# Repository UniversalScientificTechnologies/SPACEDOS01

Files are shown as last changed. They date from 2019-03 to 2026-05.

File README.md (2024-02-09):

# SPACEDOS01B - Cosmic-ray spectrometer and dosimeter for unmanned spacecraft missions

SPACEDOS01B is a semiconductor-based dosimeter launched at Sokrat-R (NORAD ID 44404) satellite, currently orbiting the Earth about 500km above the surface.
The device is intended for the measurement of cosmic radiation in mixed ionization fields on board satellites. In the case of manned missions look to [SPACEDOS02](https://github.com/UniversalScientificTechnologies/SPACEDOS02) or [SPACEDOS03](https://github.com/UniversalScientificTechnologies/SPACEDOS03).

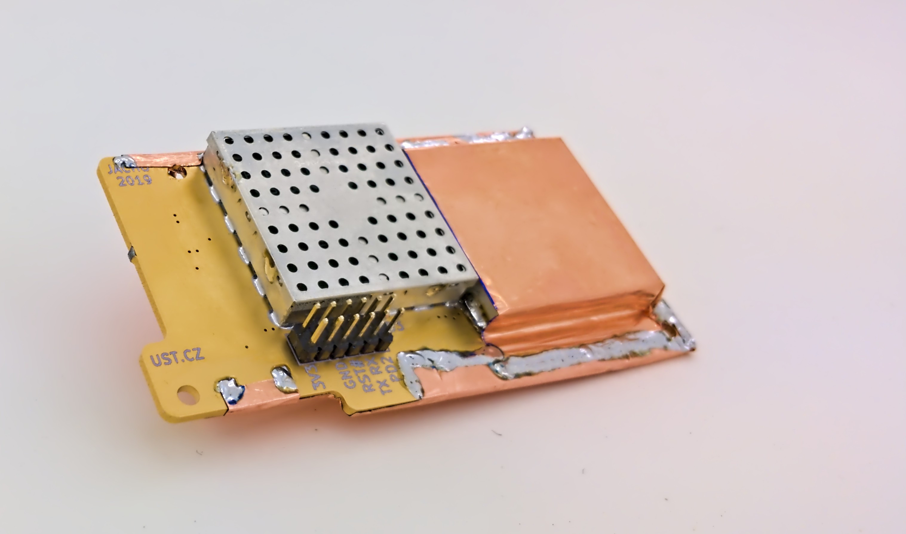
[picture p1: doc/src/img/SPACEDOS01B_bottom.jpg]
SPACEDOS01B device from bottom side PCB

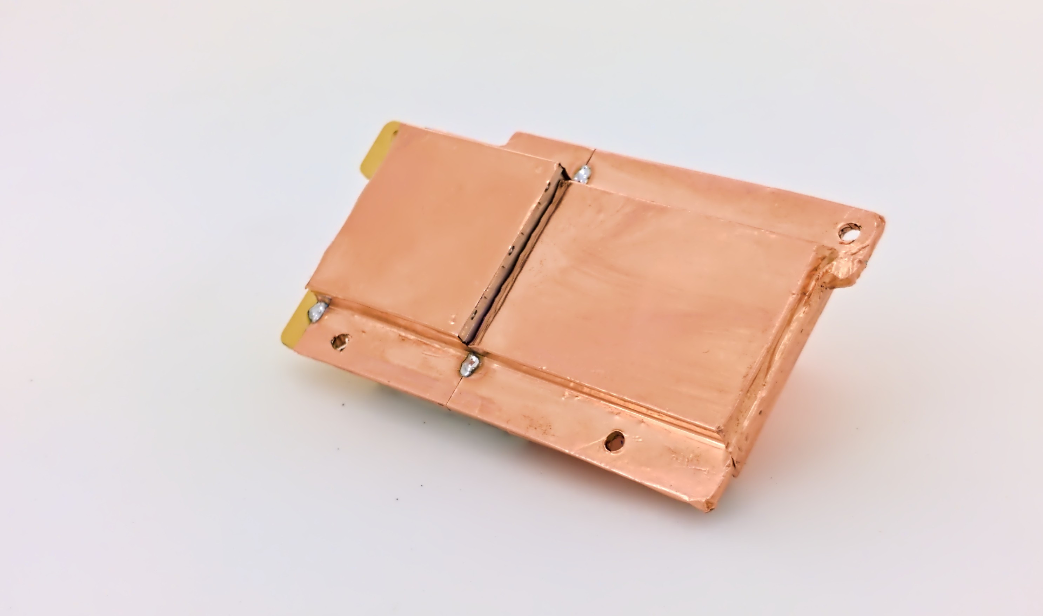
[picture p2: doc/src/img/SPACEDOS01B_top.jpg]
SPACEDOS01B device from top side PCB


The device can be purchased from Universal Scientific Technologies s.r.o. Contact us by email at sale@ust.cz for a commercial quotation.

### The main technical parameters are the following

* Silicon PIN diode detector with ~12.5 mm³ detection volume
* Measurement environment: vacuum < 3.2×10e−2 Pa
* Number of energy channels: 250
* Deposited energy range: from 200 keV to 12 MeV
* Energy measurement resolution: < 50 keV/channel
* Power supply: 3.3 V / 3 mA
* Integration time: 15 s
* Interface: RS232 TTL
* Dimensions(HxWxL): 15mm x 41mm x 94 mm
* Weight 33 g

[Technical documentation](https://docs.dos.ust.cz/spacedos/SPACEDOS01)

## References

  * [SPACEDOS dosimeter from the NPI became a part of the Cosmos Discovery exhibition](http://www.ujf.cas.cz/en/news/SPACEDOS-dosimeter-from-the-NPI-became-a-part-of-the-Cosmos-Discovery-exhibition/)
  * [SPACEDOS an open-source PIN diode dosimeter for applications in Space](https://indico.ujf.cas.cz/event/2/contributions/27/attachments/25/46/Po-1315-Kakona-774711333.pdf)

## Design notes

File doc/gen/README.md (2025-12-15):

# PCB

Board size: 93.5x48.16 mm (3.68x1.9 inches)

- This is the size of the rectangle that contains the board
- Thickness: 1.6 mm (63 mils)
- Material: FR4
- Finish: HAL
- Layers: 2
- Copper thickness: 35 µm

Solder mask: TOP / BOTTOM

- Color: Green

Silk screen: TOP / BOTTOM

- Color: White

# Important sizes

Clearance: 0.2 mm (8 mils)

Track width: 0.25 mm (10 mils)

- By design rules: 0.2 mm (8 mils)

Drill: 0.5 mm (20 mils)

- Vias: 0.5 mm (20 mils) [Design: 0.4 mm (16 mils)]
- Pads: 0.85 mm (33 mils)
- The above values are real drill sizes, they add 0.1 mm (4 mils) to plated holes (PTH)

Via: 0.8/0.4 mm (31/16 mils)

- By design rules: 0.8/0.3 mm (31/12 mils)
- Micro via: yes [0.2/0.1 mm (8/4 mils)]
- Buried/blind via: yes
- Total: 188 (thru: 188 buried/blind: 0 micro: 0)

Outer Annular Ring: 0.15 mm (6 mils)

- By design rules: 0.26 mm (10 mils)

Eurocircuits class: 4B
- Using min drill 0.5 mm for an OAR of 0.15 mm

# General stats

Components count: (SMD/THT)

- Top: 73/9 (SMD + THT)
- Bottom: 2/8 (SMD + THT)

Defined tracks:

- 0.3 mm (12 mils)
- 0.4 mm (16 mils)
- 0.5 mm (20 mils)
- 0.6 mm (24 mils)
- 0.7 mm (28 mils)
- 0.8 mm (31 mils)

Used tracks:

- 0.25 mm (10 mils) (67) defined: no
- 0.3 mm (12 mils) (84) defined: yes
- 0.4 mm (16 mils) (246) defined: yes
- 0.5 mm (20 mils) (2) defined: yes
- 0.6 mm (24 mils) (34) defined: yes
- 0.8 mm (31 mils) (54) defined: yes

Defined vias:

Used vias:

- 0.8/0.4 mm (31/16 mils) (Count: 188, Aspect: 2.0 A) defined: no

Holes (excluding vias):

- 0.76 mm (30 mils) (2)
- 0.89 mm (35 mils) (12)
- 3.0 mm (118 mils) (4)

Oval holes:

Drill tools (including vias and computing adjusts and rounding):

- 0.5 mm (20 mils) (188)
- 0.85 mm (33 mils) (2)
- 1.0 mm (39 mils) (12)
- 3.1 mm (122 mils) (4)

Solder paste stats:

Using a paste with 87.75 % alloy, that has an specific gravity for the alloy of 7.4 g/cm³
and 1.0 g/cm³ for the flux. This paste has an specific gravity of  4.15 g/cm³.

The stencil thickness is  0.12 mm.

| Side   | Pads with paste | Area [mm²] | Paste [g] |
|--------|-----------------|------------|-----------|
| Top    |             280 |     466.08 |      2.32 |
| Bottom |              56 |     166.40 |      0.83 |
| Total  |             336 |     632.48 |      3.15 |

Note: this is just an approximation to the theoretical value. Margins of the solder mask and waste aren't computed.

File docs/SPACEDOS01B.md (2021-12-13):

---
layout: default
title: SPACEDOS01B
nav_order: 0
parent: SPACEDOS01
permalink: SPACEDOS01B
---

# SPACEDOS
## Physical dimensions
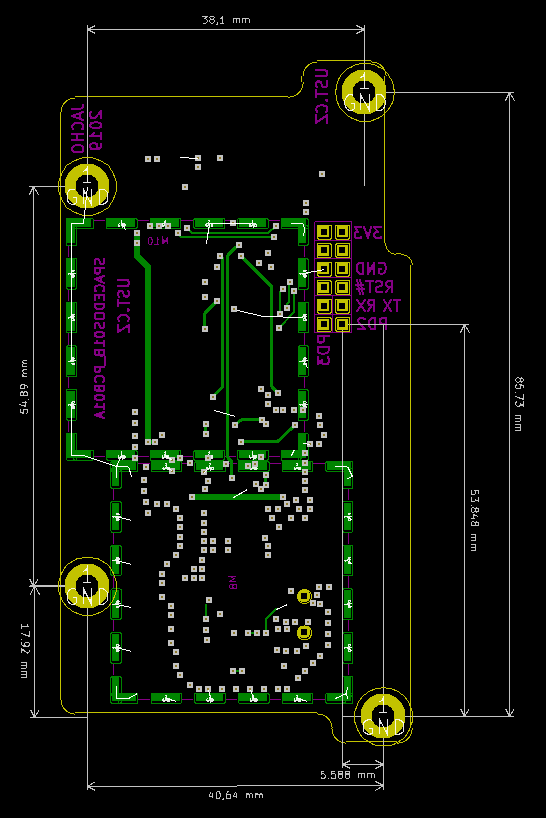
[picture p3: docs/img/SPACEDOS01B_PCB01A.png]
Physical dimensions


## Energetic range and Climatic endurance
 
 * Dissipated Energy range: from 100 keV to 9 MeV (divided into 8 logarithmic channels)
 * Energy Resolution: < 50 keV
 * Integration Time: 15 s
 * Temperature Stability: from -50 ℃ to +50 ℃ within error +50 keV
 * Used Sensor: HAMAMATSU S11773-02 (PIN diode 5 x 5 x 0.5 mm<sup>3</sup>)
 * Weight: 33 g

## Electrical interface
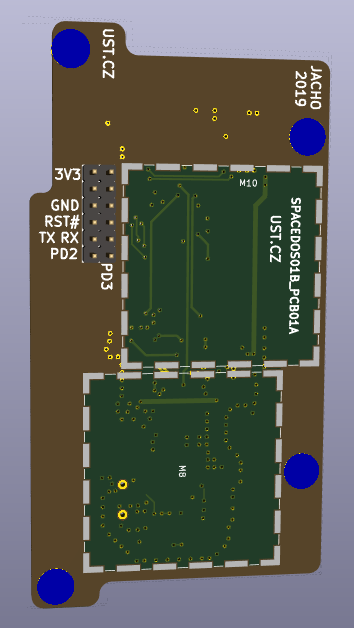
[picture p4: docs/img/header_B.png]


Conector is depicted from PIN's side.

Signal | Description
--- | ---
PD2 |  Universal Input pin
PD3 |  Universal Output pin
RX0 |  RS232 Receive (3.3 V)
TX0 |  RS232 Transmit (3.3 V)
RST# | Reset (trough capacitor)
GND |  Ground
3V3 |  Power supply +3.3 V

Power consumption: 2.6 mA from 3.3 V

## Communication protocol
### Sample of output data
```
$POSD,2a1c18d43c3937e40a3beb6c2855589b2d1a19e9
$ICSD
$DPSD,98,7fbd,36,1,0,0,0,0,0,0,100
$HKSD,9,98,800b,fe,0,0,7fbd,36,1,0,0,0,0,0,0,0,0,0,0,0,0,0,0,0,0,0,0,0,0,0,0,0,0,0,0,0,0,0,0,0,0,0,0,0,0,0,0,0,0,0,0,0,0,0
$BESD,4,e7,2,1,0,0,0,0,0
$ADSD,d3,3,0,0,0,0
```

SPACEDOS sends `$DPSD`, `$HKSD` and `$BESD` messages each cca 15 seconds.
`$ADSD` message is sended ones per one day.

Communication speed is 2400 baud.

### Power On
_It transmits just after power on._

```
#POSD, <git hash>
```

Value | Length | Type |Note
--- | --- | --- | ---
`$POSD` | 5 B | [Char](https://github.com/ODZ-UJF-AV-CR/SPACEDOS01/wiki/Char) | Header
git hash | 20 B | [Hex](https://github.com/ODZ-UJF-AV-CR/SPACEDOS01/wiki/Hex) | Git hash tag from source file

This information just says hello after power on.

### Initiation complete
_It transmits ones after initialisation after power on._

```
#ICSD
```

Initiation of the SPACEDOS HW is done.
Initiation is completed up to one second after power on.

### DPSD - SpaceDos Data Payload message
_It transmits every 15 seconds._

```
$DPSD, <uptime>, <noise channel>, <0.1 MeV>, <0.14 MeV>, <0.21 MeV>, <0.33 MeV>, <0.66 MeV>, <1.68 MeV>, <4.72 MeV>, <'>=9 MeV'>, <DC offset>
```

Value | Length | Type |Note
--- | --- | --- | ---
$DPSD | 5 B | [Char](https://github.com/ODZ-UJF-AV-CR/SPACEDOS01/wiki/Char) | Header
uptime | 4 B | [Hex](https://github.com/ODZ-UJF-AV-CR/SPACEDOS01/wiki/Hex) | Time from power on
noise channel | 2 B | [Hex](https://github.com/ODZ-UJF-AV-CR/SPACEDOS01/wiki/Hex) | this channel containing noise
0.1 MeV | 2 B | [Hex](https://github.com/ODZ-UJF-AV-CR/SPACEDOS01/wiki/Hex) | number of particles with absorbed energy above 0.1 MeV
... | ... | ... |
'>=9' MeV | 2 B | [Hex](https://github.com/ODZ-UJF-AV-CR/SPACEDOS01/wiki/Hex) | Overrange particles
DC offset | 2 B | [Hex](https://github.com/ODZ-UJF-AV-CR/SPACEDOS01/wiki/Hex) | Offset of ADC

This messages should be stored for long period and transmited to the ground as a batch.

Minimal data payload (without timemark) is 18 B per 15 s => 103680 B per day

### HKSD - SpaceDos HouseKeeping message
_It transmits every 15 seconds._

```
$HKSD, <measurement No.> , <uptime>, <filter suppressions>, <position of the 1-st channel>, <1-st ch.>, <2-nd ch.>, <3-rd ch.>,...
``` 

There is a packet with housekeeping information. Transmission of this packet is done besides other experiments hosekeeping data. Total length of this packet should be shorten. 

Value | Range | type |Note
--- | --- | --- | ---
$HKSD | fix | [Char](https://github.com/ODZ-UJF-AV-CR/SPACEDOS01/wiki/Char) | Header
measurement No. | 0..65535 | [Hex](https://github.com/ODZ-UJF-AV-CR/SPACEDOS01/wiki/Hex) |
uptime | 0..4294967295 | [Hex](https://github.com/ODZ-UJF-AV-CR/SPACEDOS01/wiki/Hex) |
filter suppressions | 0..65535 | [Hex](https://github.com/ODZ-UJF-AV-CR/SPACEDOS01/wiki/Hex) | Number of ussage of digital filter for double peak suppression
position of the 1-st channel | 0..511 | [Hex](https://github.com/ODZ-UJF-AV-CR/SPACEDOS01/wiki/Hex) |
1-st ch. | 0..65535 | [Hex](https://github.com/ODZ-UJF-AV-CR/SPACEDOS01/wiki/Hex) | Number of events in 1-st ch.
2-nd ch. | 0..65535 |  [Hex](https://github.com/ODZ-UJF-AV-CR/SPACEDOS01/wiki/Hex) |Number of events in 2-nd ch.
... | ... |
50-th ch. | 0..65535 |  [Hex](https://github.com/ODZ-UJF-AV-CR/SPACEDOS01/wiki/Hex) |Number of events in 50-th ch.

### BESD - SpaceDos BEacon message
_It transmits every 15 seconds. Values are zeroed after sending ADSD message._

```
$BESD,<counter>, <0.1 MeV>, <0.14 MeV>, <0.21 MeV>, <0.33 MeV>, <0.66 MeV>, <1.68 MeV>, <4.72 MeV>, <'>=9 MeV'>
```

This message contains cumulative data for beacon transmission.

Value | Length | Type |Note
--- | --- | --- | ---
$BESD | 5 B | [Char](https://github.com/ODZ-UJF-AV-CR/SPACEDOS01/wiki/Char) | Header
counter | 2 B | [Hex](https://github.com/ODZ-UJF-AV-CR/SPACEDOS01/wiki/Hex) | Number of the beacon message
0.1 MeV | 2 B | [Hex](https://github.com/ODZ-UJF-AV-CR/SPACEDOS01/wiki/Hex) | number of particles with absorbed energy above 0.1 MeV
0.14 MeV | 2 B | [Hex](https://github.com/ODZ-UJF-AV-CR/SPACEDOS01/wiki/Hex) | number of particles with absorbed energy above 0.14 MeV
... | ... | ... |
'>=9' MeV | 2 B | [Hex](https://github.com/ODZ-UJF-AV-CR/SPACEDOS01/wiki/Hex) | Overrange particles

### ADSD - SpaceDos Almanac Data message
_It transmits after 5760 beacon messages. (cca every one day)_

```
$ADSD, <0.1 MeV 1 day old>, <0.14 MeV one day old>, <0.66 MeV one day old>, <0.1 MeV two days old>, <0.14 MeV two days old>, <0.66 MeV two days old>
```

This message contains two days old data for the beacon transmission purposes.

Value | Length | Type |Note
--- | --- | --- | ---
$ADSD | 5 B | [Char](https://github.com/ODZ-UJF-AV-CR/SPACEDOS01/wiki/Char) | Header
0.1 MeV one day old | 4 B | [Hex](https://github.com/ODZ-UJF-AV-CR/SPACEDOS01/wiki/Hex) | number of particles with absorbed energy above 0.1 MeV one day before
0.14 MeV one day old | 4 B | [Hex](https://github.com/ODZ-UJF-AV-CR/SPACEDOS01/wiki/Hex) | number of particles with absorbed energy above 0.14 MeV one day before
0.66 MeV one day old | 4 B | [Hex](https://github.com/ODZ-UJF-AV-CR/SPACEDOS01/wiki/Hex) | number of particles with absorbed energy above 0.66 MeV one day before
0.1 MeV two days old | 4 B | [Hex](https://github.com/ODZ-UJF-AV-CR/SPACEDOS01/wiki/Hex) | number of particles with absorbed energy above 0.1 MeV two days before
0.14 MeV two days old | 4 B | [Hex](https://github.com/ODZ-UJF-AV-CR/SPACEDOS01/wiki/Hex) | number of particles with absorbed energy above 0.14 MeV two days before
0.66 MeV two days old | 4 B | [Hex](https://github.com/ODZ-UJF-AV-CR/SPACEDOS01/wiki/Hex) | number of particles with absorbed energy above 0.66 MeV two days before

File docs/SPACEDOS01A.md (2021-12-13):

---
layout: default
title: SPACEDOS01A
nav_order: 0
parent: SPACEDOS01
permalink: SPACEDOS01A
---

# SPACEDOS
## Physical dimensions
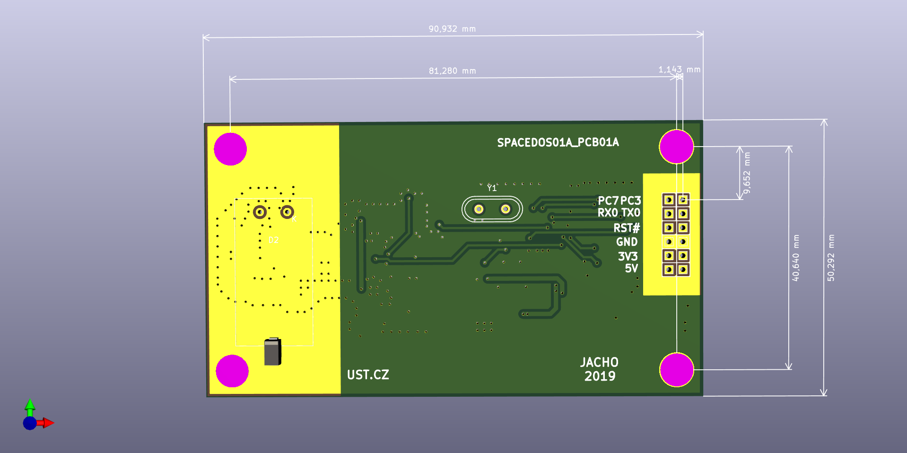
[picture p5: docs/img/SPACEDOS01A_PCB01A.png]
Physical dimensions


## Energetic range and Climatic endurance

 * Dissipated Energy range: from 200 keV to 9 MeV
 * Energy Resolution: < 50 keV
 * Temperature Stability: from -50 ℃ to +50 ℃ within error +50 keV
 * Used Sensor: HAMAMATSU S11773-02 (PIN diode 5 x 5 x 0.5 mm<sup>3</sup>)

## Electrical interface
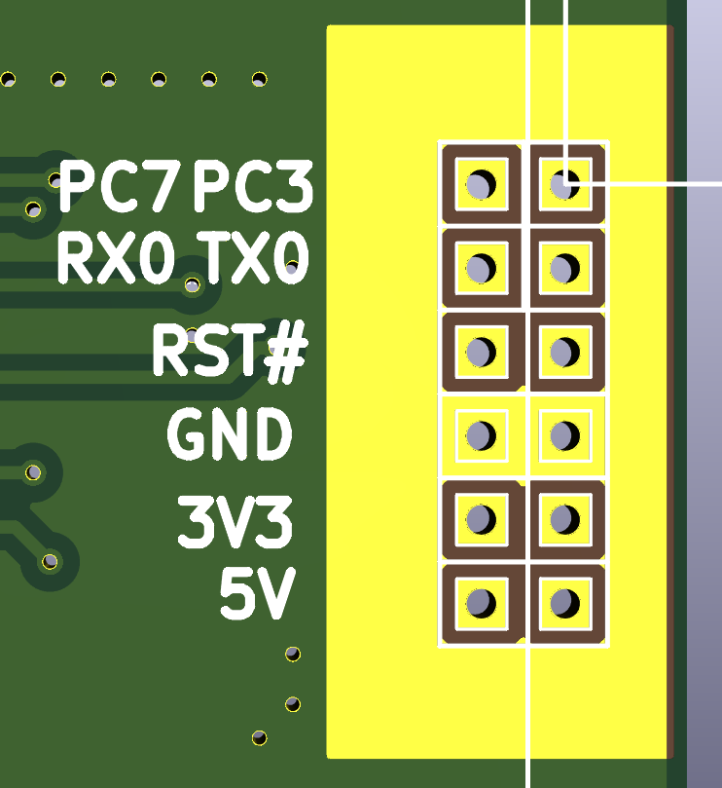
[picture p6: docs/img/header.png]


Signal | Description
--- | ---
PC7 |  Universal IO pin
PC3 |  Universal IO pin
RX0 |  RS232 Receive (3.3 V)
TX0 |  RS232 Transmit (3.3 V)
RST# | Reset (trough capacitor)
GND |  Ground
3V3 |  Power supply +3.3 V
5V  |  Internally connected to +3.3 V

Power consumption: 2.6 mA from 3.3 V

## Communication protocol
### Sample of output data
```
#Cvak...
#Hmmm...
$DPSD,00000f08,7fc5,002f,0000,0000,0001,0000,0000,0000,0000,0100
$HKSD,244,3848,32778,254,0,0,32709,47,0,0,0,0,0,0,1,0,0,0,0,0,0,0,0,0,0,0,0,0,0,0,0,0,0,0,0,0,0,0,0,0,0,0,0,0,0,0,0,0,0,0,0,0,0,0
$BESD,0004,0000010e,00000000,00000000,00000001,00000000,00000000,00000000,00000000
$ADSD,000000de,00000003,00000000,0000011d,00000000,00000000
```
SPACEDOS sends $DPSD, $HKSD and $BESD messages each cca 15 seconds.
$ADSD message is sended ones per one day.

Communication speed is 2400 baud.

### Power On

`#Cvak…`

This information just says hello after power on.

### Initiation complete

`#Hmmm...`

Initiation of the SPACEDOS HW is done.
Initiation is completed up to one second after power on.

### DPSD - SpaceDos Data Payload message

`
$DPSD, <uptime>, <noise channel>, <0.1 MeV>, <0.14 MeV>, <0.21 MeV>, <0.33 MeV>, <0.66 MeV>, <1.68 MeV>, <4.72 MeV>, <'>=9 MeV'>, <DC offset>`

Value | Length | Type |Note
--- | --- | --- | ---
$DPSD | 5 B | Char | Header
uptime | 4 B | Hex | Time from power on
noise channel | 2 B | Hex | this channel containing noise
0.1 MeV | 2 B | Hex | number of particles with absorbed energy above 0.1 MeV
... | ... | ... |
'>=9' MeV | 2 B | Hex | Overrange particles
DC offset | 2 B | Hex | Offset of ADC

This messages should be stored for long period and transmited to the ground as a batch.

Minimal data payload (without timemark) is 18 B per 15 s => 103680 B per day

### HKSD - SpaceDos HouseKeeping message

`$HKSD, <measurement No.> , <uptime>, <filter suppressions>, <position of the 1-st channel>, <1-st ch.>, <2-nd ch.>, <3-rd ch.>,...` 

There is a packet with housekeeping information. Transmission of this packet is done besides other experiments hosekeeping data. Total length of this packet should be shorten. 

Value | Range | type |Note
--- | --- | --- | ---
$HKSD | fix | Char | Header
measurement No. | 0..65535 | Dec |
uptime | 0..4294967295 | Dec |
filter suppressions | 0..65535 | Dec | Number of ussage of digital filter for double peak suppression
position of the 1-st channel | 0..511 | Dec |
1-st ch. | 0..65535 | Dec | Number of events in 1-st ch.
2-nd ch. | 0..65535 |  Dec |Number of events in 2-nd ch.
... | ... |
50-th ch. | 0..65535 |  Dec |Number of events in 50-th ch.

### BESD - SpaceDos BEacon message

`$BESD,<counter>, <0.1 MeV>, <0.14 MeV>, <0.21 MeV>, <0.33 MeV>, <0.66 MeV>, <1.68 MeV>, <4.72 MeV>, <'>=9 MeV'>`

This message contains cumulative data for beacon transmission.

Value | Length | Type |Note
--- | --- | --- | ---
$BESD | 5 B | Char | Header
counter | 2 B | Hex | Number of the beacon message
0.1 MeV | 2 B | Hex | number of particles with absorbed energy above 0.1 MeV
0.14 MeV | 2 B | Hex | number of particles with absorbed energy above 0.14 MeV
... | ... | ... |
'>=9' MeV | 2 B | Hex | Overrange particles

### ADSD - SpaceDos Almanac Data message

`$ADSD, <0.1 MeV 1 day old>, <0.14 MeV one day old>, <0.66 MeV one day old>, <0.1 MeV two days old>, <0.14 MeV two days old>, <0.66 MeV two days old>`

This message contains two days old data for the beacon transmission purposes.

Value | Length | Type |Note
--- | --- | --- | ---
$ADSD | 5 B | Char | Header
0.1 MeV one day old | 4 B | Hex | number of particles with absorbed energy above 0.1 MeV one day before
0.14 MeV one day old | 4 B | Hex | number of particles with absorbed energy above 0.14 MeV one day before
0.66 MeV one day old | 4 B | Hex | number of particles with absorbed energy above 0.66 MeV one day before
0.1 MeV two days old | 4 B | Hex | number of particles with absorbed energy above 0.1 MeV two days before
0.14 MeV two days old | 4 B | Hex | number of particles with absorbed energy above 0.14 MeV two days before
0.66 MeV two days old | 4 B | Hex | number of particles with absorbed energy above 0.66 MeV two days before

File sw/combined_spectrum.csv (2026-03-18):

Channel | Count
-2 | 765
-1 | 201135
0 | 799245
1 | 129183
2 | 48
3 | 7
4 | 6
5 | 12
6 | 57
7 | 113
8 | 68
9 | 80
10 | 86
11 | 58
12 | 75
13 | 85
14 | 52
15 | 69
16 | 44
17 | 72
18 | 55
19 | 42
20 | 52
21 | 11
22 | 3
23 | 0
24 | 0
25 | 1
26 | 0
27 | 0
28 | 4
29 | 1
30 | 0
31 | 0
32 | 0
33 | 3
34 | 0
35 | 3
36 | 1
37 | 2
38 | 2
39 | 5
40 | 0
41 | 1
42 | 3
43 | 4
44 | 6
45 | 22
46 | 33
47 | 27
48 | 21
49 | 48
50 | 26
51 | 22
52 | 25
53 | 22
54 | 27
55 | 23
56 | 18
57 | 25
58 | 25
59 | 18
60 | 14
61 | 20
62 | 25
63 | 22
64 | 13
65 | 31
66 | 19
67 | 20
68 | 23
69 | 19
70 | 17
71 | 18
72 | 9
73 | 15
74 | 20
75 | 15
76 | 16
77 | 24
78 | 18
79 | 22
80 | 8
81 | 19
82 | 13
83 | 14
84 | 12
85 | 20
86 | 16
87 | 16
88 | 17
89 | 12
90 | 22
91 | 10
92 | 20
93 | 24
94 | 14
95 | 3
96 | 1
97 | 6
98 | 2
99 | 0
100 | 3
101 | 3
102 | 4
103 | 3
104 | 2
105 | 4
106 | 1
107 | 2
108 | 3
109 | 1
110 | 5
111 | 2
112 | 3
113 | 4
114 | 6
115 | 2
116 | 1
117 | 3
118 | 6
119 | 2
120 | 2
121 | 3
122 | 5
123 | 2
124 | 1
125 | 4
126 | 1
127 | 1
128 | 1
129 | 1
130 | 3
131 | 0
132 | 1
133 | 2
134 | 3
135 | 2
136 | 7
137 | 16
138 | 60
139 | 85
140 | 190
141 | 386
142 | 102
143 | 10
144 | 0
145 | 1
146 | 1
147 | 3
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

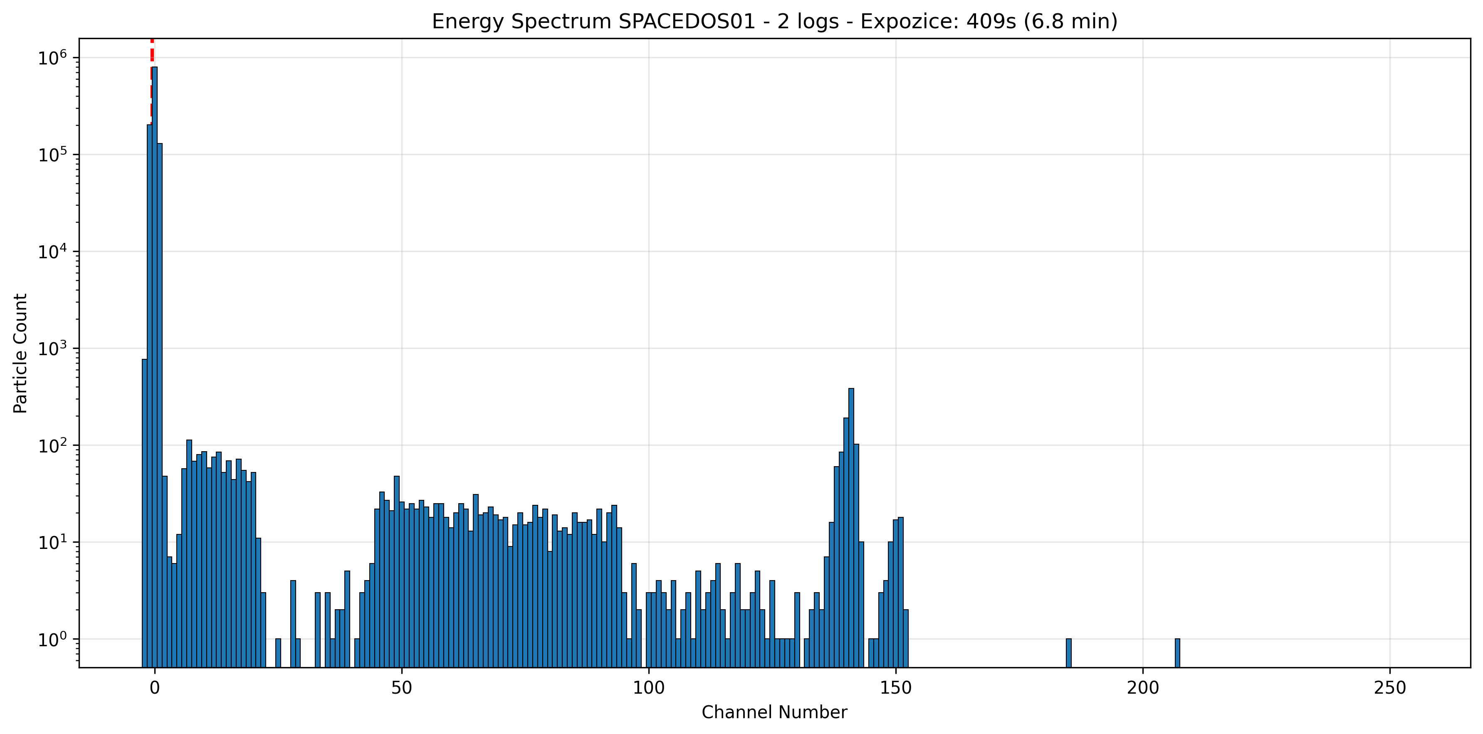
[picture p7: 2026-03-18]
sw/combined_spectrum.png

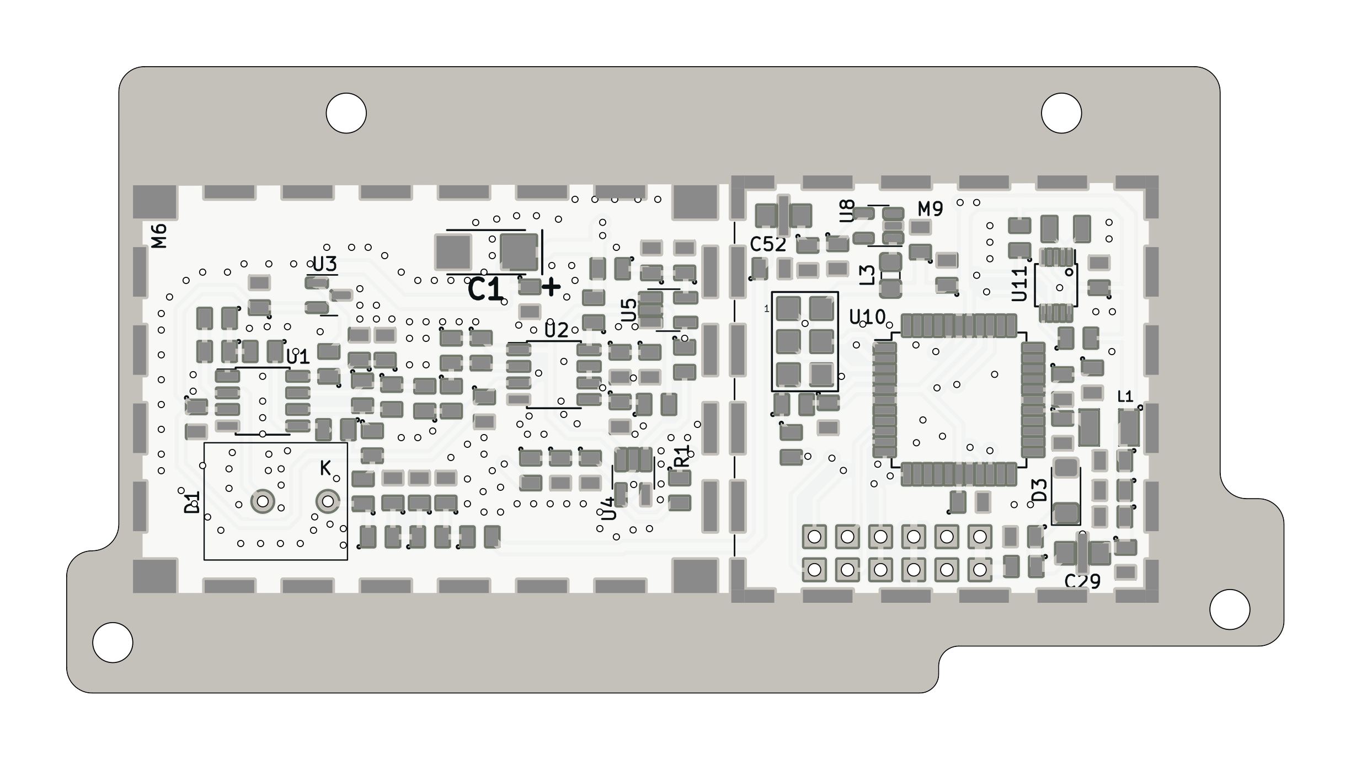
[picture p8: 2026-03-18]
doc/gen/img/SPACEDOS01-top.png

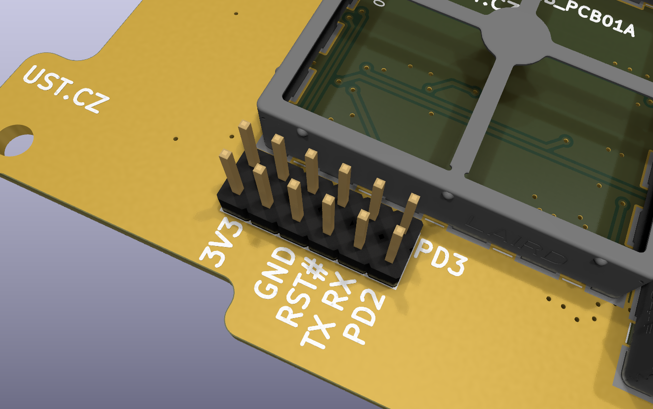
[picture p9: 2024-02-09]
doc/src/img/header_B.png

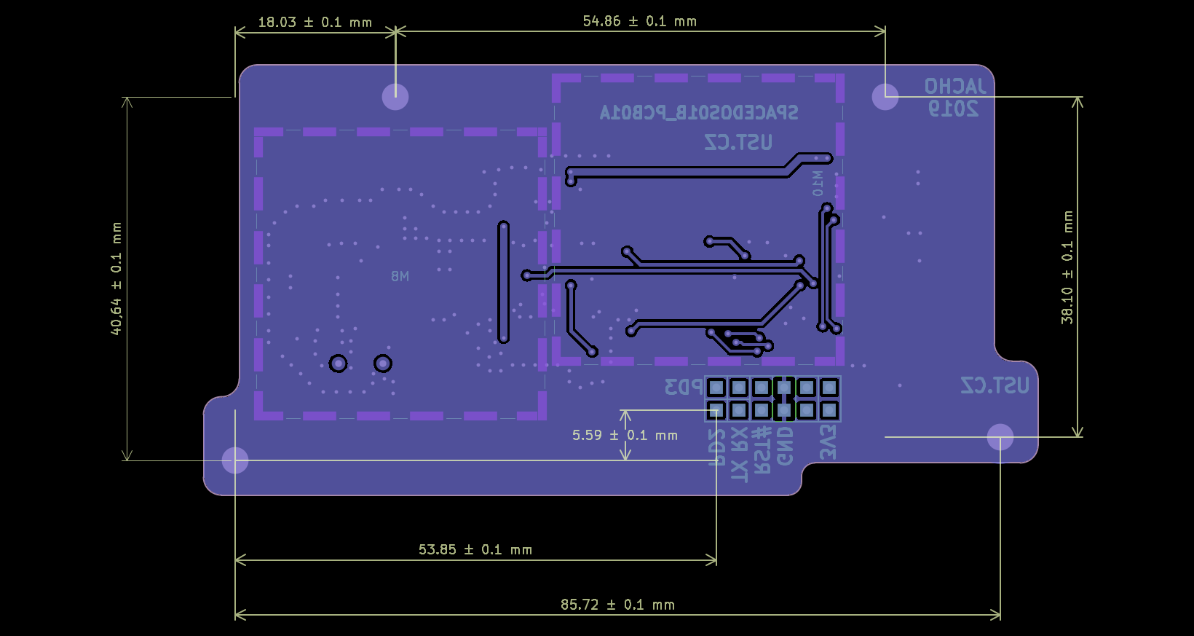
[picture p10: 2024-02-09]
doc/src/img/SPACEDOS01B_PCB01A.png

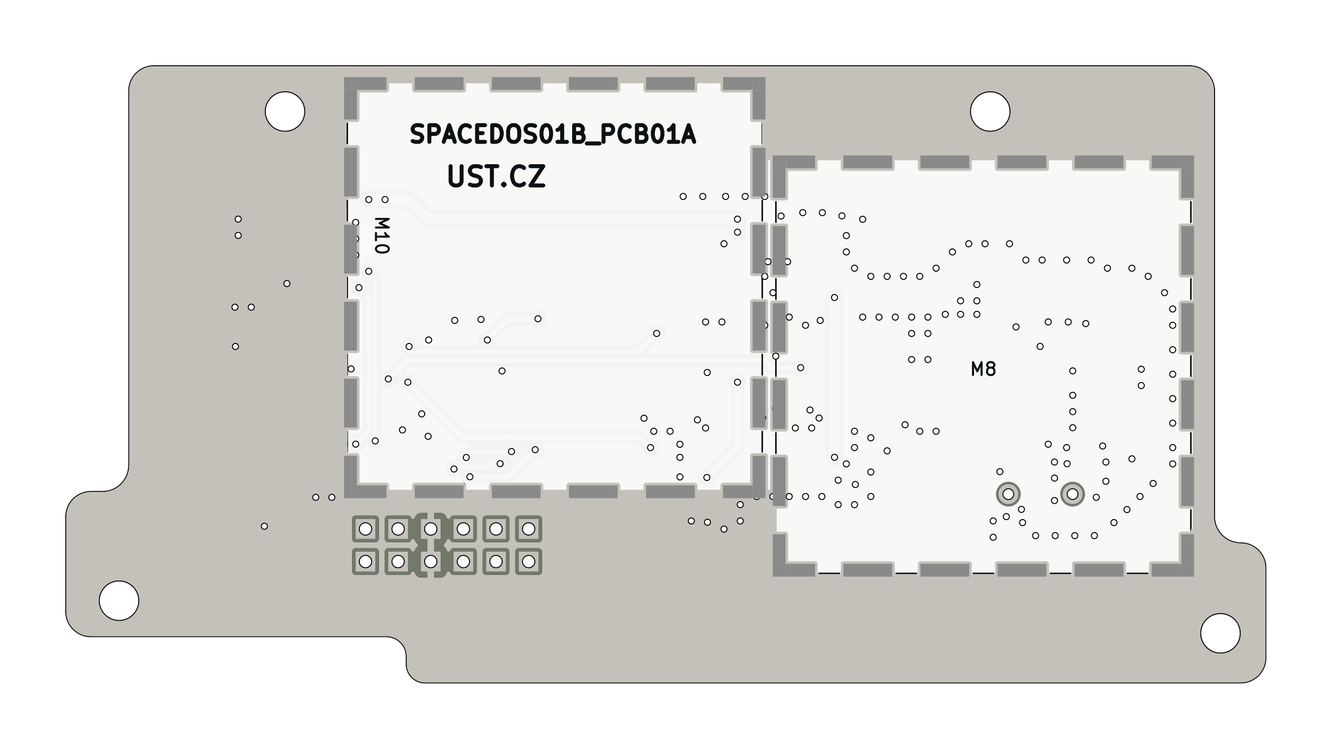
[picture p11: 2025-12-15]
doc/gen/img/SPACEDOS01-bottom.png

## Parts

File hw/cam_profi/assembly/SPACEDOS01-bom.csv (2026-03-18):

Component | Description | Part | References | Value | Footprint | Quantity Per PCB | Datasheet | ust_id
1 |  | C | C18 | 2n2 | SMD-0805 | 1 | ~ | 5c70984712875079b91f8b46
2 |  | C | C15 | 3n3 | SMD-0805 | 1 | ~ | 5c70984712875079b91f8b47
3 |  | C | C2C10C11C12C13C14C16C20 | 100nF | SMD-0805 | 8 |  | 5c70984712875079b91f8b4c
4 |  | C-device-DATALOGGER01A-rescue-CCP2019V01A-rescue-SPACEDOS01A_PCB01A-rescue | C26C27C28C31C32C34C35C39C44C47C54C55 | 100nF | SMD-0805 | 12 |  | 5c70984712875079b91f8b4c
5 |  | C | C24 | 1uF | SMD-0805 | 1 | ~ | 5c70984712875079b91f8b50
6 |  | C | C3C17 | 4u7 | SMD-0805 | 2 | ~ | 5e3ff8fc1287502a33bad7a3
7 |  | C-device-DATALOGGER01A-rescue-CCP2019V01A-rescue-SPACEDOS01A_PCB01A-rescue | C43 | 4u7 | SMD-0805 | 1 |  | 5e3ff8fc1287502a33bad7a3
8 |  | C | C4C6C7C8C9C21C23 | 10uF | SMD-0805 | 7 | ~ | 5c70984712875079b91f8b53
9 |  | C-device-DATALOGGER01A-rescue-CCP2019V01A-rescue-SPACEDOS01A_PCB01A-rescue | C36C40C42C50 | 10uF | SMD-0805 | 4 |  | 5c70984712875079b91f8b53
10 |  | CP | C1 | 22uF | TantalC_SizeC_Reflow | 1 | ~ | 650b58f1462c6d9e7205463b
11 |  | C | C19 | 1nF/NP0 | SMD-0805 | 1 | ~ | 5c70984812875079b91f8ba6
12 |  | C | C5 | 1pFNP0 251R15S1R0AV4E | SMD-0805 | 1 | ~ | 5c70984712875079b91f8b9f
13 |  | EMI_Filter_C-device-DATALOGGER01A-rescue-CCP2019V01A-rescue-SPACEDOS01A_PCB01A-rescue | C29C52 | NFM21PC105-1uF | FIR_0805 | 2 | http://www.murata.com/~/media/webrenewal/support/library/catalog/products/emc/emifil/c31e.ashx?la=en-gb | 5c70984412875079b91f880f
14 |  | D-device-DATALOGGER01A-rescue-CCP2019V01A-rescue-SPACEDOS01A_PCB01A-rescue | D3 | BZV55C-5,6V | D_MiniMELF | 1 |  | 5c70984512875079b91f88b2
15 |  | D_Photo | D1 | S2744-09 | HAMAMATSU_S11773-02 | 1 | ~ | 628d118cdc56076e9a2235e4
16 |  | Polyfuse-device-DATALOGGER01A-rescue-CCP2019V01A-rescue-SPACEDOS01A_PCB01A-rescue-SPACEDOS01B_PCB01A-rescue | F2 | 2R2 | SMD-0805 | 1 |  | 5cac42d21287500e61c241e5
17 |  | L-device-DATALOGGER01A-rescue-CCP2019V01A-rescue-SPACEDOS01A_PCB01A-rescue | L1 | 10uH - LQH32CN100K23L | SMD-1210 | 1 |  | 5c70984412875079b91f87ff
18 |  | L_Small | L3 | DFE252012P-4R7M | R_0805_2012Metric_Pad1.15x1.40mm_HandSolder | 1 | ~ | 5cc3309d128750448e54e8d8
19 |  | HOLE | M8M9M10 | BMI-S-204-F | Laird_Technologies_BMI-S-204-F_32.00x32.00mm | 3 |  | 5c72751c1287500b4e11301a
20 |  | HOLE | M6 | BMI-S-210-F | BMI-S-210-F | 1 |  | 5c70984312875079b91f873d
21 |  | R | R1 | 10R | SMD-0805 | 1 | ~ | 5c70984512875079b91f896d
22 |  | R | R2R3R4R5 | 470R | SMD-0805 | 4 | ~ | 5c70984512875079b91f8986
23 |  | R | R8 | 1k | SMD-0805 | 1 | ~ | 5c70984512875079b91f898c
24 |  | R | R10 | 1k2 | SMD-0805 | 1 | ~ | 5c70984512875079b91f898d
25 |  | R | R13 | 2k2 | SMD-0805 | 1 | ~ | 5c70984612875079b91f8990
26 |  | R | R9R11R15R19R22 | 4k7 | SMD-0805 | 5 | ~ | 5c70984612875079b91f8995
27 |  | R | R7R12 | 10k | SMD-0805 | 2 | ~ | 5c70984612875079b91f899f
28 |  | R-device-DATALOGGER01A-rescue-CCP2019V01A-rescue-SPACEDOS01A_PCB01A-rescue | R20R21R23 | 10k | SMD-0805 | 3 |  | 5c70984612875079b91f899f
29 |  | R | R6 | 10M | SMD-0805 | 1 | ~ | 5c70984712875079b91f8aae
30 |  | ATMEGA1284P-AU-atmel-DATALOGGER01A-rescue-CCP2019V01A-rescue-SPACEDOS01A_PCB01A-rescue | U10 | ATMEGA1284P-AU | TQFP-44_10x10mm_P0.8mm | 1 | http://www.atmel.com/Images/Atmel-8272-8-bit-AVR-microcontroller-ATmega164A_PA-324A_PA-644A_PA-1284_P_datasheet.pdf | 5c70984712875079b91f8b5b
31 |  | ISL21070CIH320Z-TK | U3 | ISL21080DIH312Z-TK 1V25 | SOT-23 | 1 | https://eu.mouser.com/datasheet/2/698/REN_isl21080_DST_20040119-1998038.pdf | 5c70984712875079b91f8b7a
32 |  | AD8692 | U1U2 | OPA2314 | SOIC-8_3.9x4.9mm_Pitch1.27mm | 2 |  | 5c70984412875079b91f879b
33 |  | PCF85263A | U11 | PCF85263A | TSSOP-10_3x3mm_Pitch0.5mm | 1 |  | 5c70984612875079b91f8a0c
34 |  | TPS61322xA | U8 | TPS613222ADBV | SOT-23-5 | 1 | https://www.ti.com/lit/ds/symlink/tps61322.pdf | 5c7190ae1287500b4e112e04
35 |  | TS5A4594 | U5 | TS5A4594 | SOT-23-5_HandSoldering | 1 |  | 5c70984612875079b91f8a0d
36 |  | OP179GRT | U4 | TS7211 | SOT-23-5_HandSoldering | 1 | http://www.analog.com/media/en/technical-documentation/data-sheets/OP179_279.pdf | 5c70984712875079b91f8b5b
37 |  | Crystal-device-DATALOGGER01A-rescue-CCP2019V01A-rescue-SPACEDOS01A_PCB01A-rescue | Y2 | ABS07-120-32.768KHZ-T | ABS07 | 1 |  | 5c70984712875079b91f8b1b

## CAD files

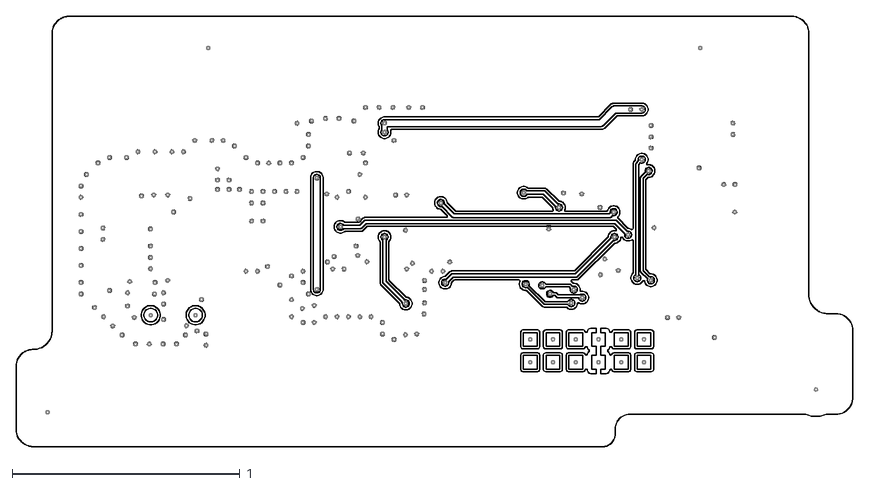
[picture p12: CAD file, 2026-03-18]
doc/gen/dxf/SPACEDOS01-B_Cu.dxf
3.68 x 1.89

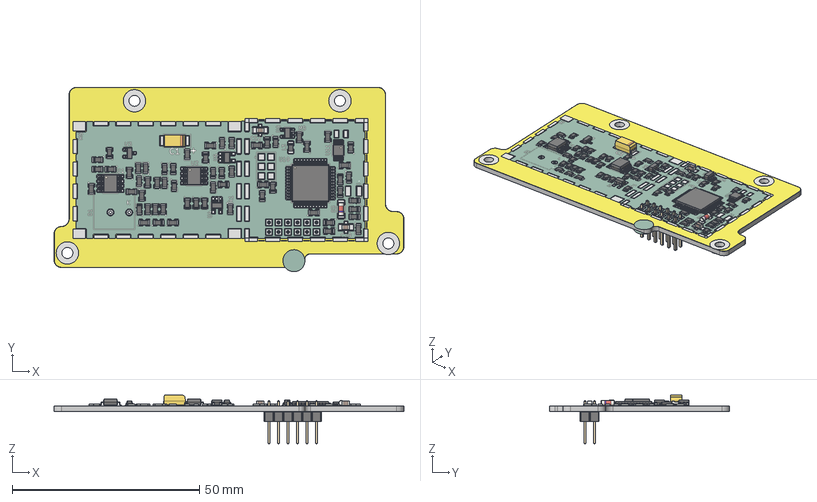
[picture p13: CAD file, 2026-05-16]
doc/gen/mesh/SPACEDOS01.step
93.5 x 49.3 x 13.0 mm
SOT-23-5 x 3
R_0805_2012Metric x 60
TQFP-44_10x10mm_P0.8mm
SOIC-8_3.9x4.9mm_P1.27mm x 2
TSSOP-10_3x3mm_P0.5mm
D_MiniMELF
SOT-23
CP_EIA-6032-28_Kemet-C
C_0805_2012Metric x 2
PinHeader_2x01_P2.54mm_Vertical
PinHeader_1x01_P2.54mm_Vertical x 4
PinHeader_1x02_P2.54mm_Vertical x 3
kibot_s5rg9nv1_copper
kibot_s5rg9nv1_pad
kibot_s5rg9nv1_via
kibot_s5rg9nv1_silkscreen x 2
kibot_s5rg9nv1_soldermask x 2
kibot_s5rg9nv1_PCB

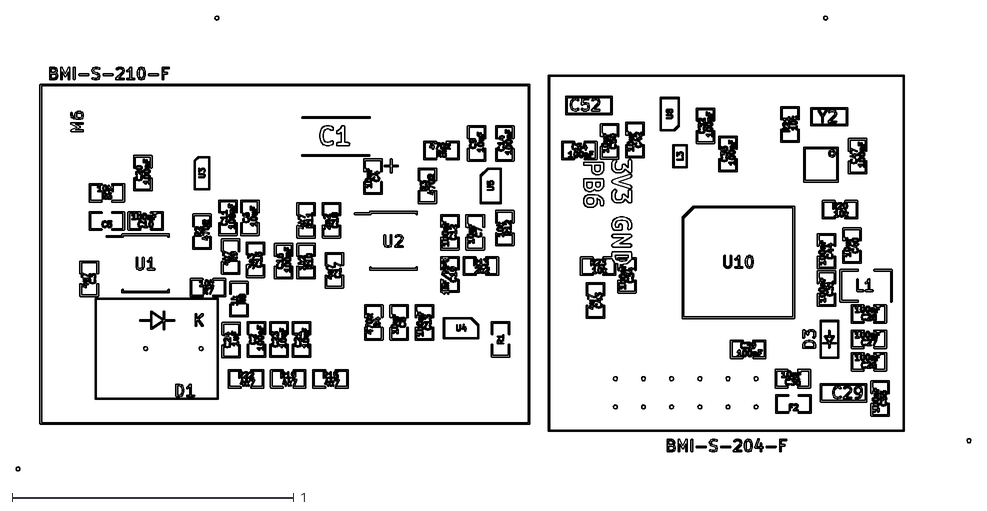
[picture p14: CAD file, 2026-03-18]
doc/gen/dxf/SPACEDOS01-F_Fab.dxf
3.39 x 1.61

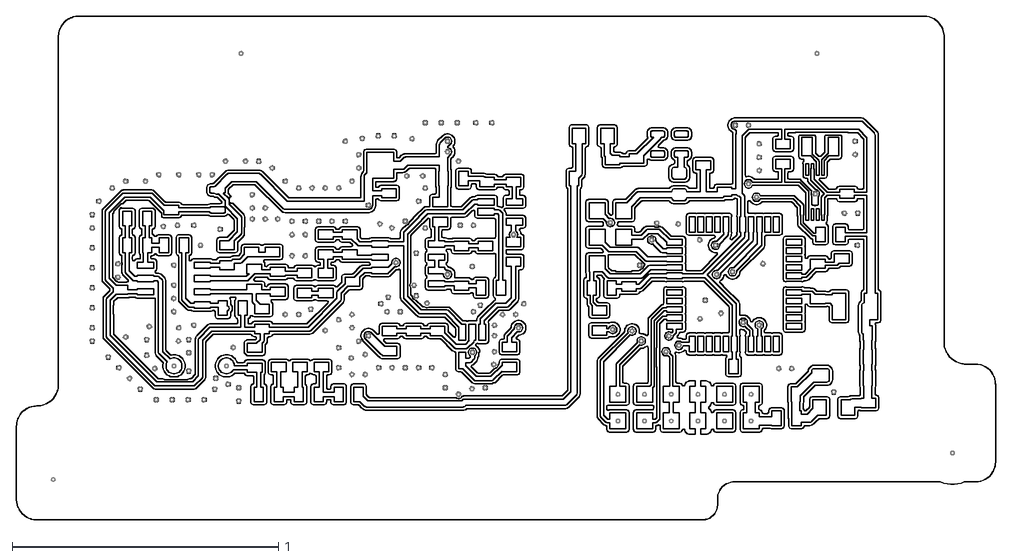
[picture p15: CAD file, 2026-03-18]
doc/gen/SPACEDOS01/dxf/SPACEDOS01-F_Cu.dxf
3.68 x 1.89

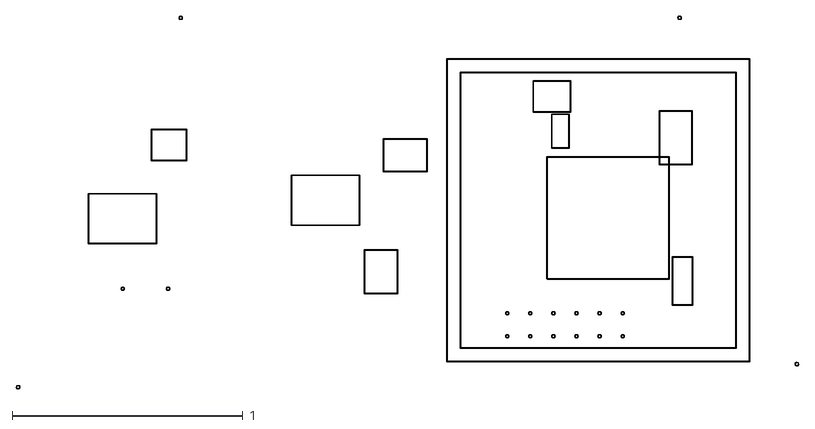
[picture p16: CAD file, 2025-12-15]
doc/gen/dxf/SPACEDOS01-F_Courtyard.dxf
3.39 x 1.61

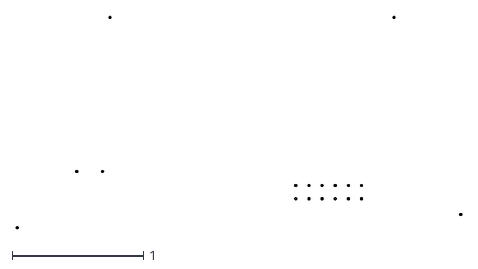
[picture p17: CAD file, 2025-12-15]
doc/gen/dxf/SPACEDOS01-Margin.dxf
3.39 x 1.61

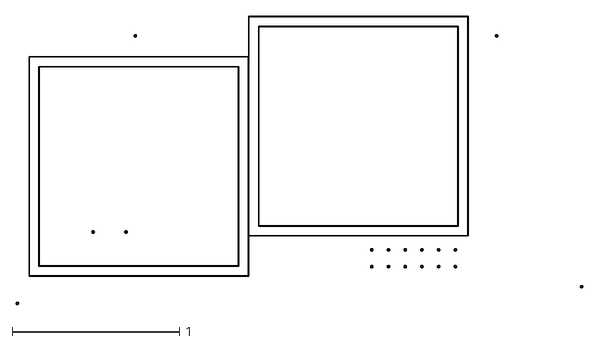
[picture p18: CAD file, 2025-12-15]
doc/gen/dxf/SPACEDOS01-B_Courtyard.dxf
3.39 x 1.72

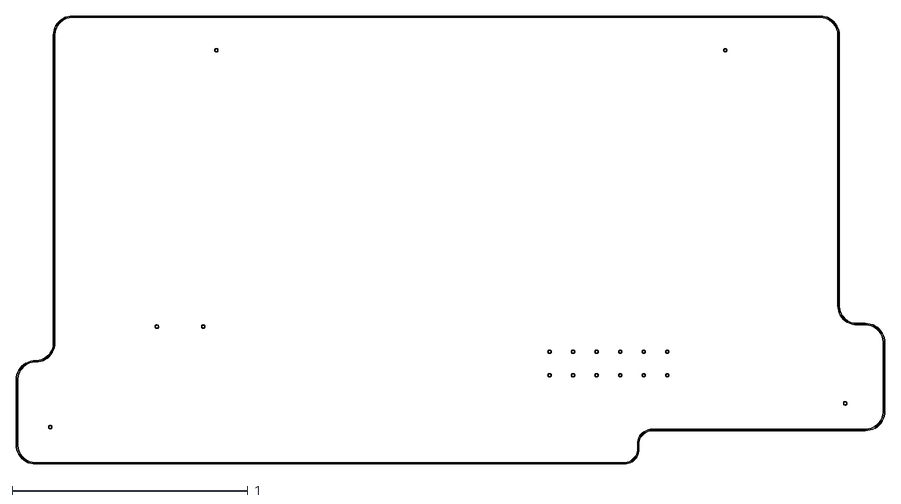
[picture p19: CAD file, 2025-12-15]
doc/gen/dxf/SPACEDOS01-Edge_Cuts.dxf
3.69 x 1.90

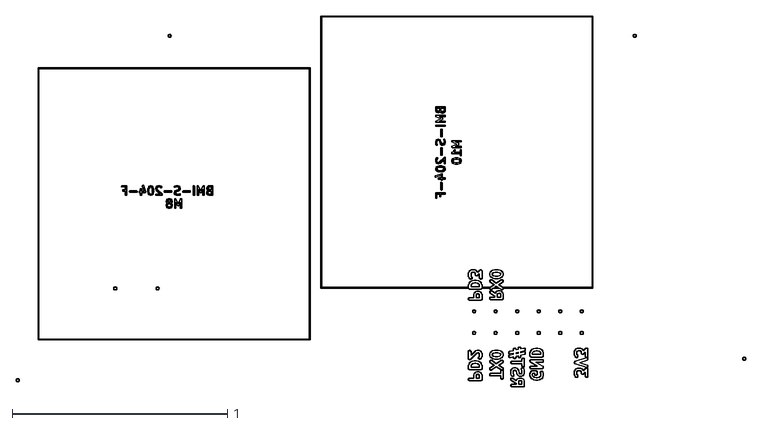
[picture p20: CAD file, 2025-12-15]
doc/gen/SPACEDOS01/dxf/SPACEDOS01-B_Fab.dxf
3.39 x 1.72

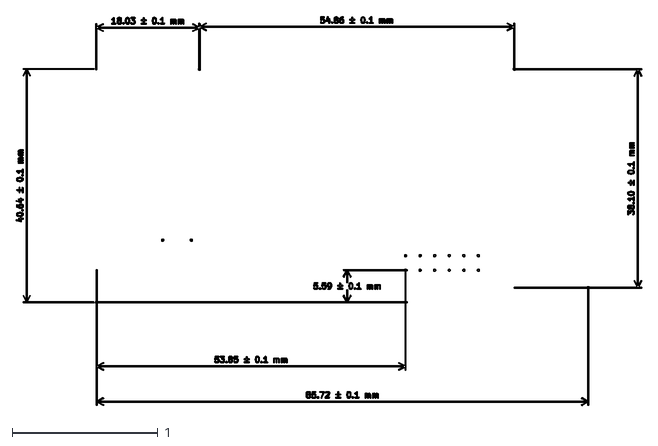
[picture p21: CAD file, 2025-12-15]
doc/gen/dxf/SPACEDOS01-User_Drawings.dxf
4.29 x 2.67

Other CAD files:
doc/gen/SPACEDOS01/mesh/SPACEDOS01.step
doc/gen/SPACEDOS01/dxf/SPACEDOS01-B_Mask.dxf
doc/gen/SPACEDOS01/dxf/SPACEDOS01-B_Paste.dxf
doc/gen/SPACEDOS01/dxf/SPACEDOS01-B_Silkscreen.dxf
doc/gen/SPACEDOS01/dxf/SPACEDOS01-F_Mask.dxf
doc/gen/SPACEDOS01/dxf/SPACEDOS01-F_Silkscreen.dxf
doc/gen/dxf/SPACEDOS01-B_Mask.dxf
doc/gen/dxf/SPACEDOS01-B_Paste.dxf
doc/gen/dxf/SPACEDOS01-B_Silkscreen.dxf
doc/gen/dxf/SPACEDOS01-F_Mask.dxf
doc/gen/dxf/SPACEDOS01-F_Silkscreen.dxf
doc/gen/mesh/SPACEDOS01.stl

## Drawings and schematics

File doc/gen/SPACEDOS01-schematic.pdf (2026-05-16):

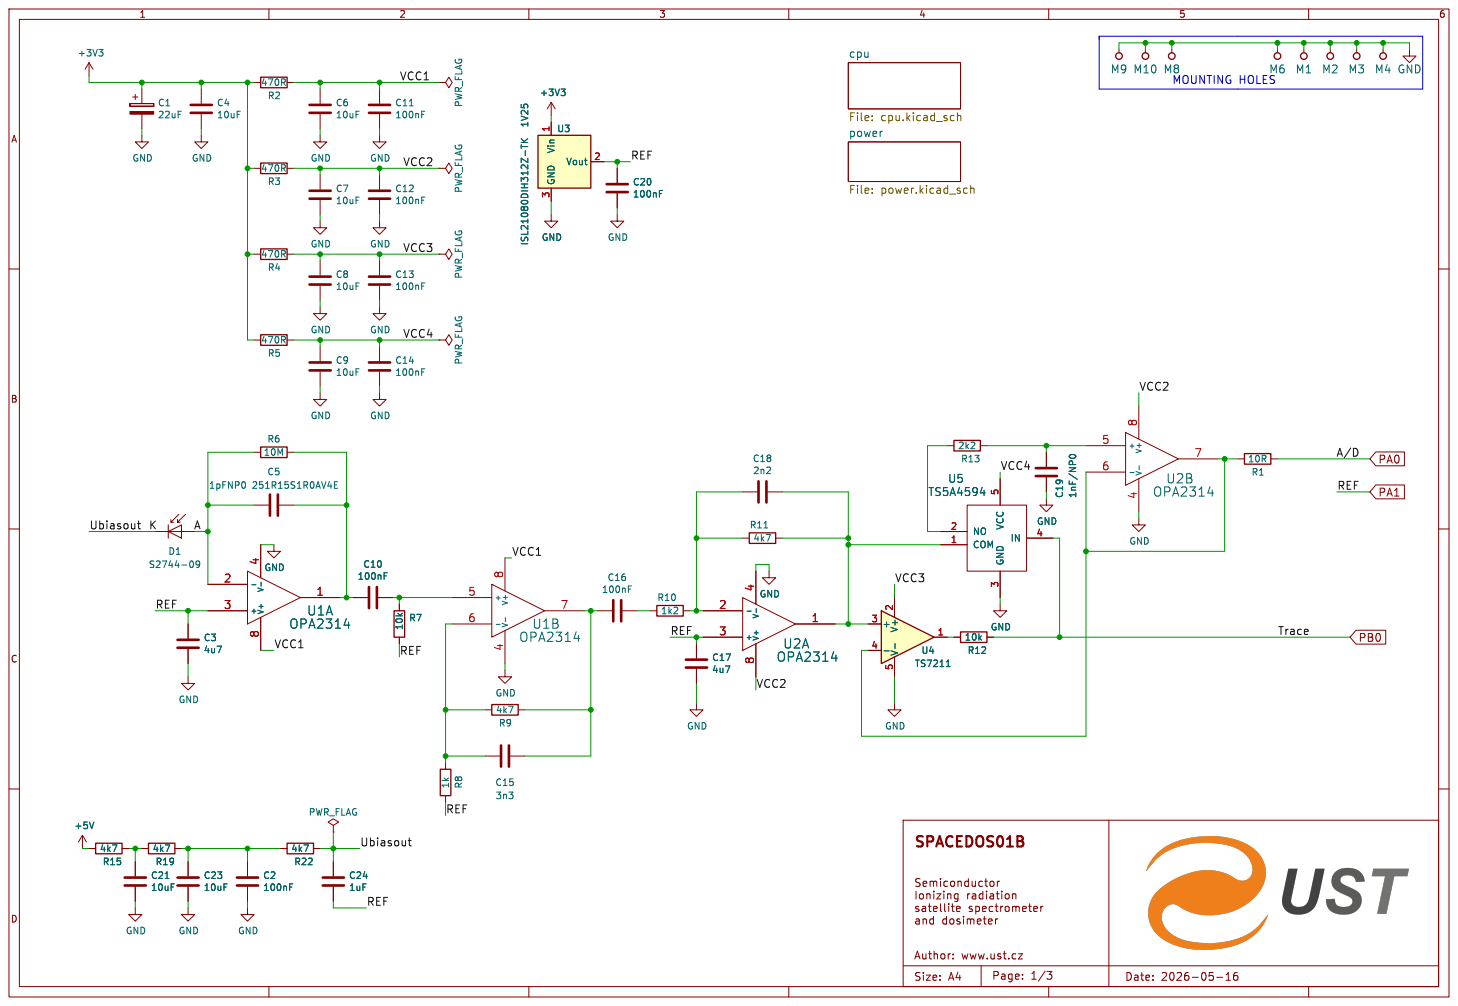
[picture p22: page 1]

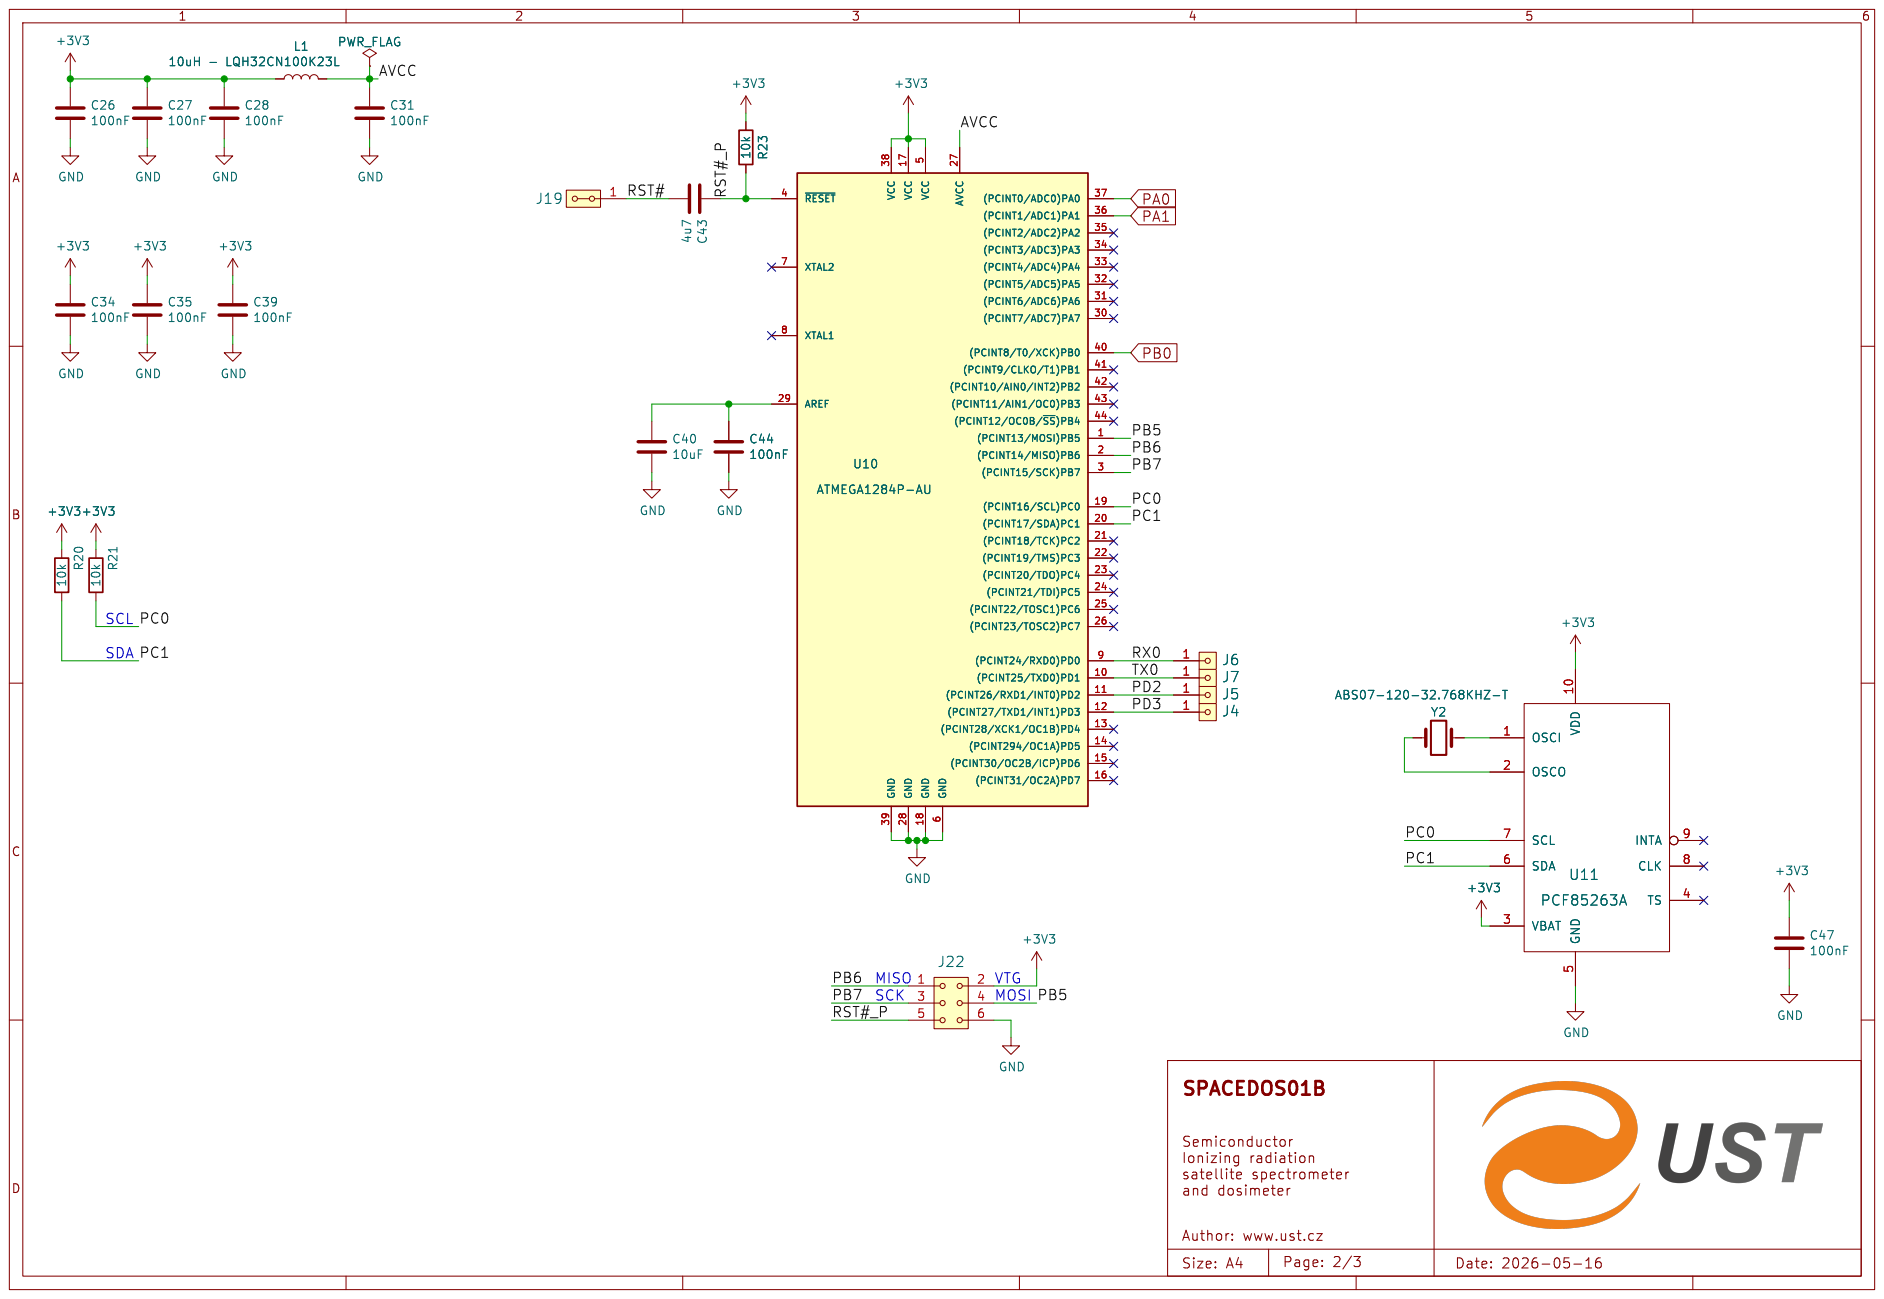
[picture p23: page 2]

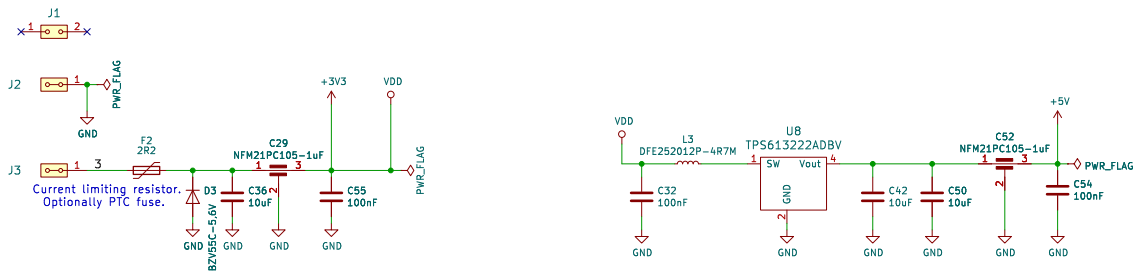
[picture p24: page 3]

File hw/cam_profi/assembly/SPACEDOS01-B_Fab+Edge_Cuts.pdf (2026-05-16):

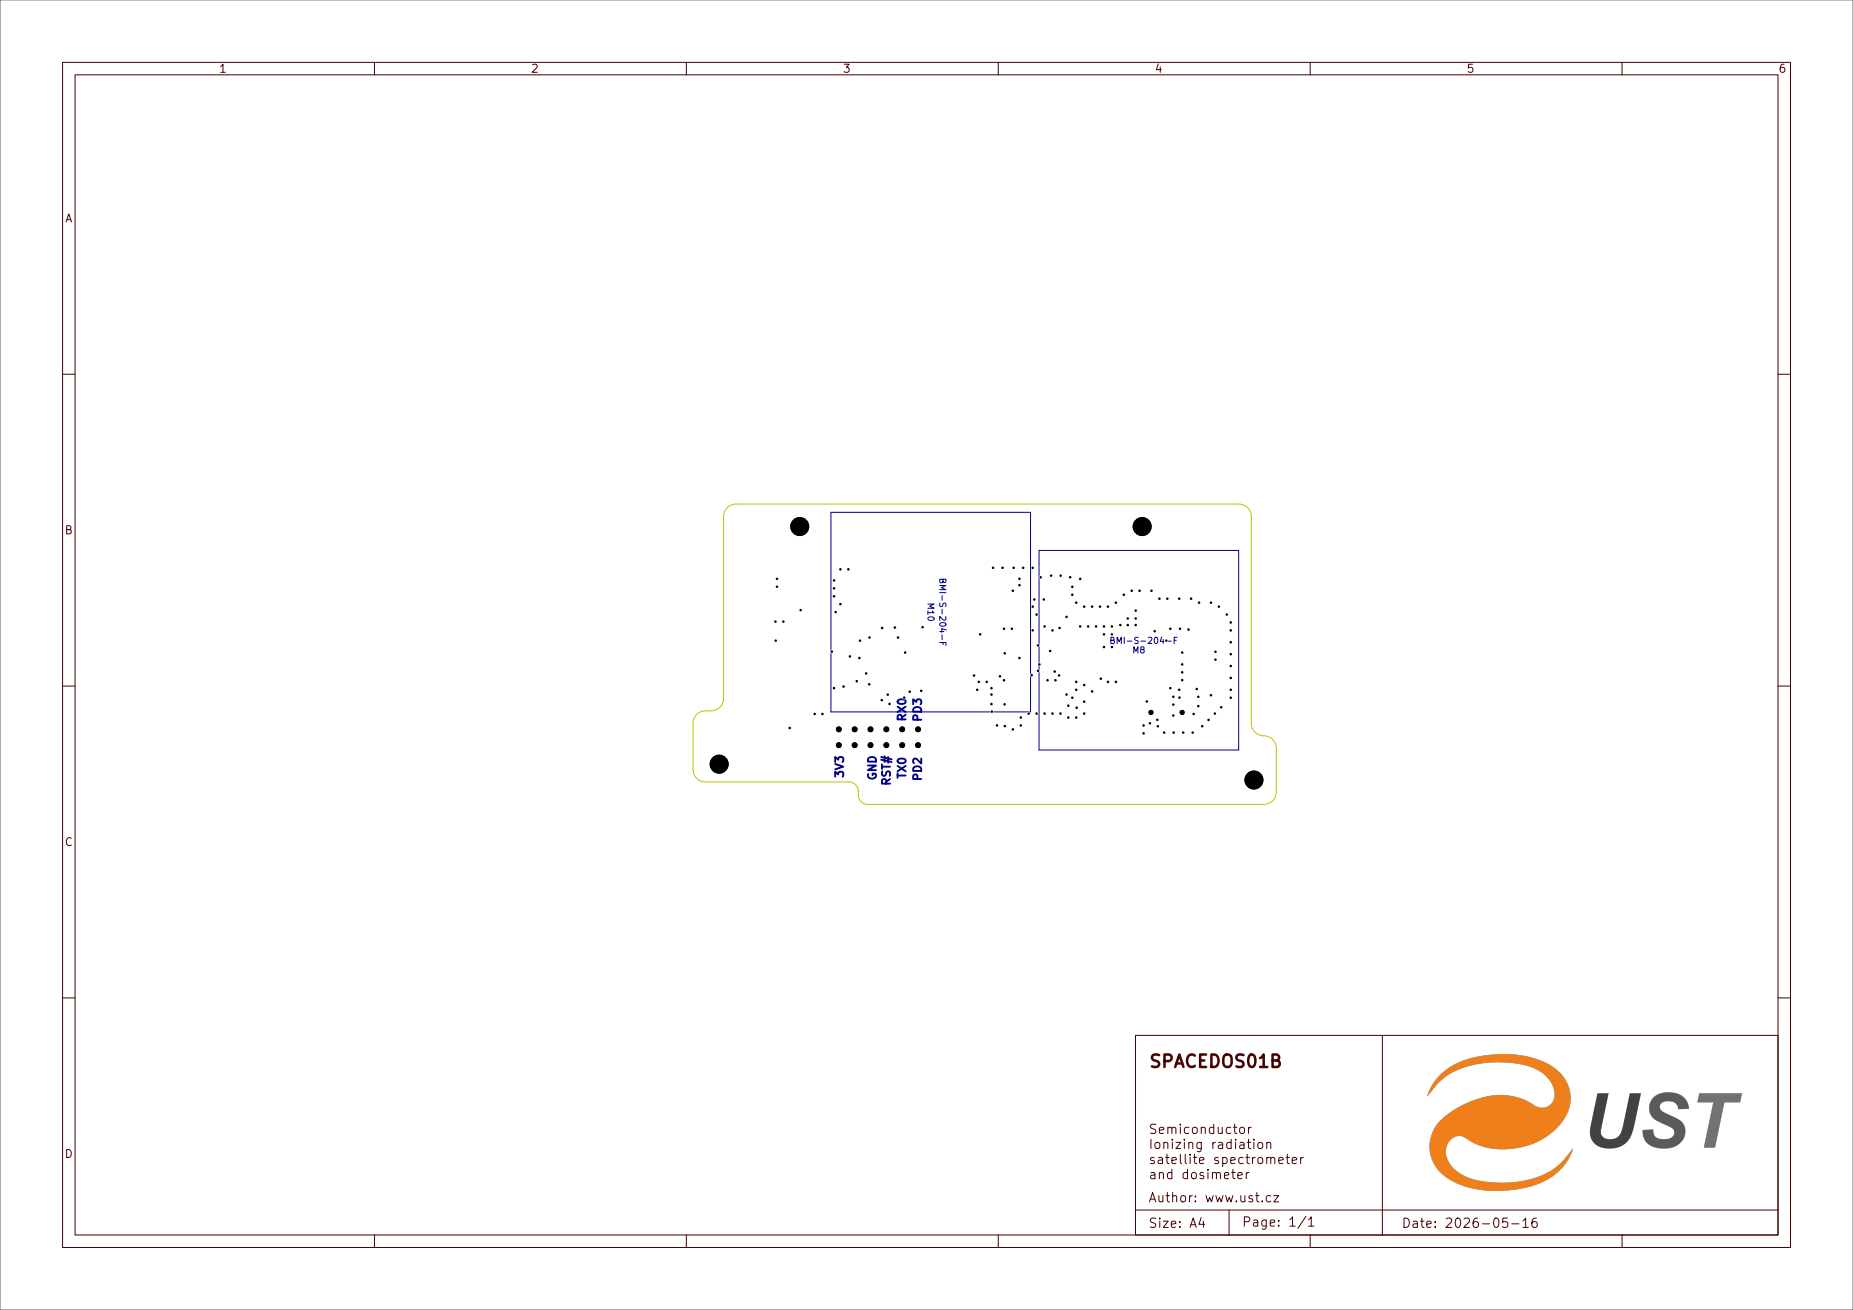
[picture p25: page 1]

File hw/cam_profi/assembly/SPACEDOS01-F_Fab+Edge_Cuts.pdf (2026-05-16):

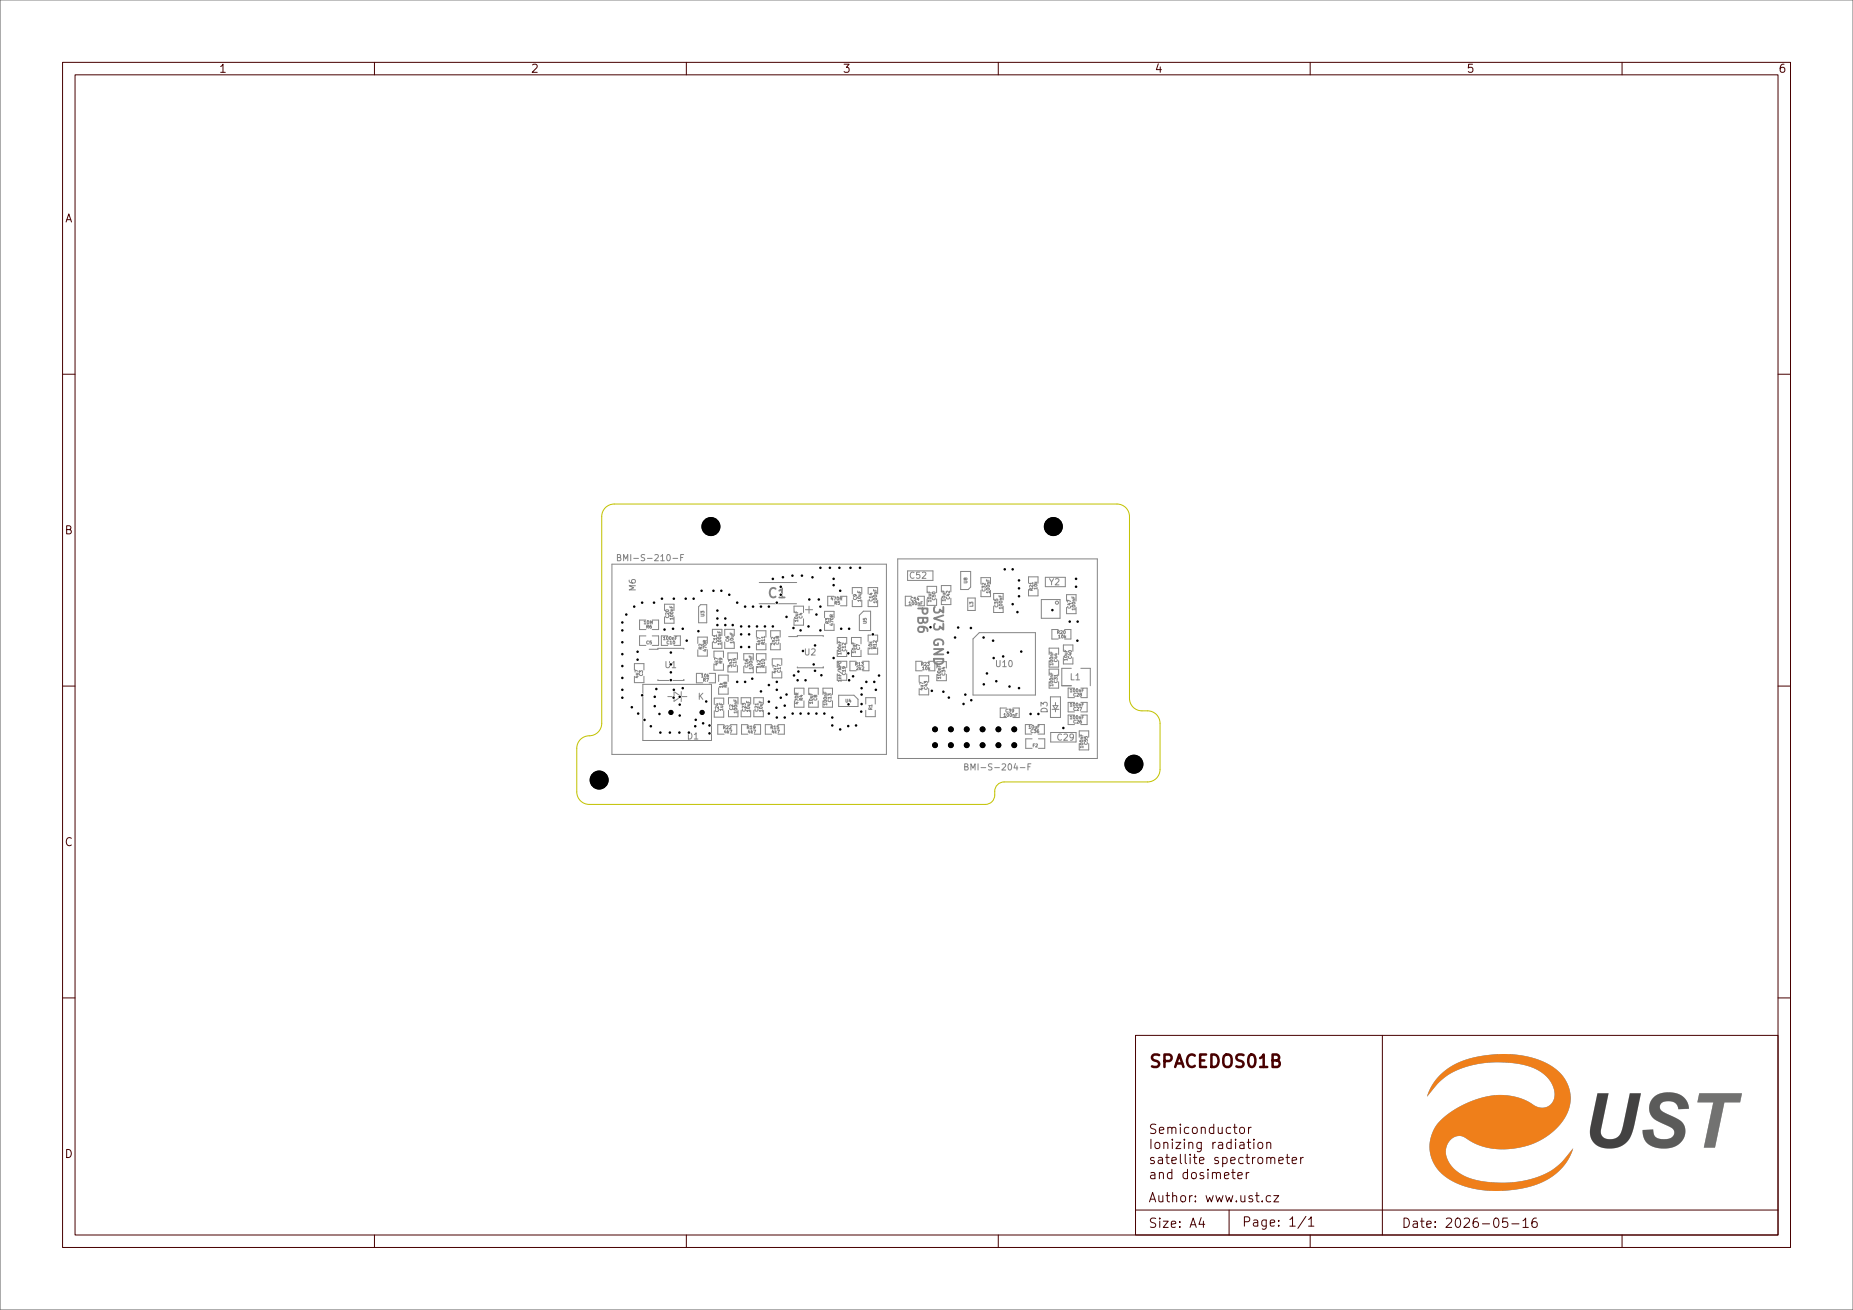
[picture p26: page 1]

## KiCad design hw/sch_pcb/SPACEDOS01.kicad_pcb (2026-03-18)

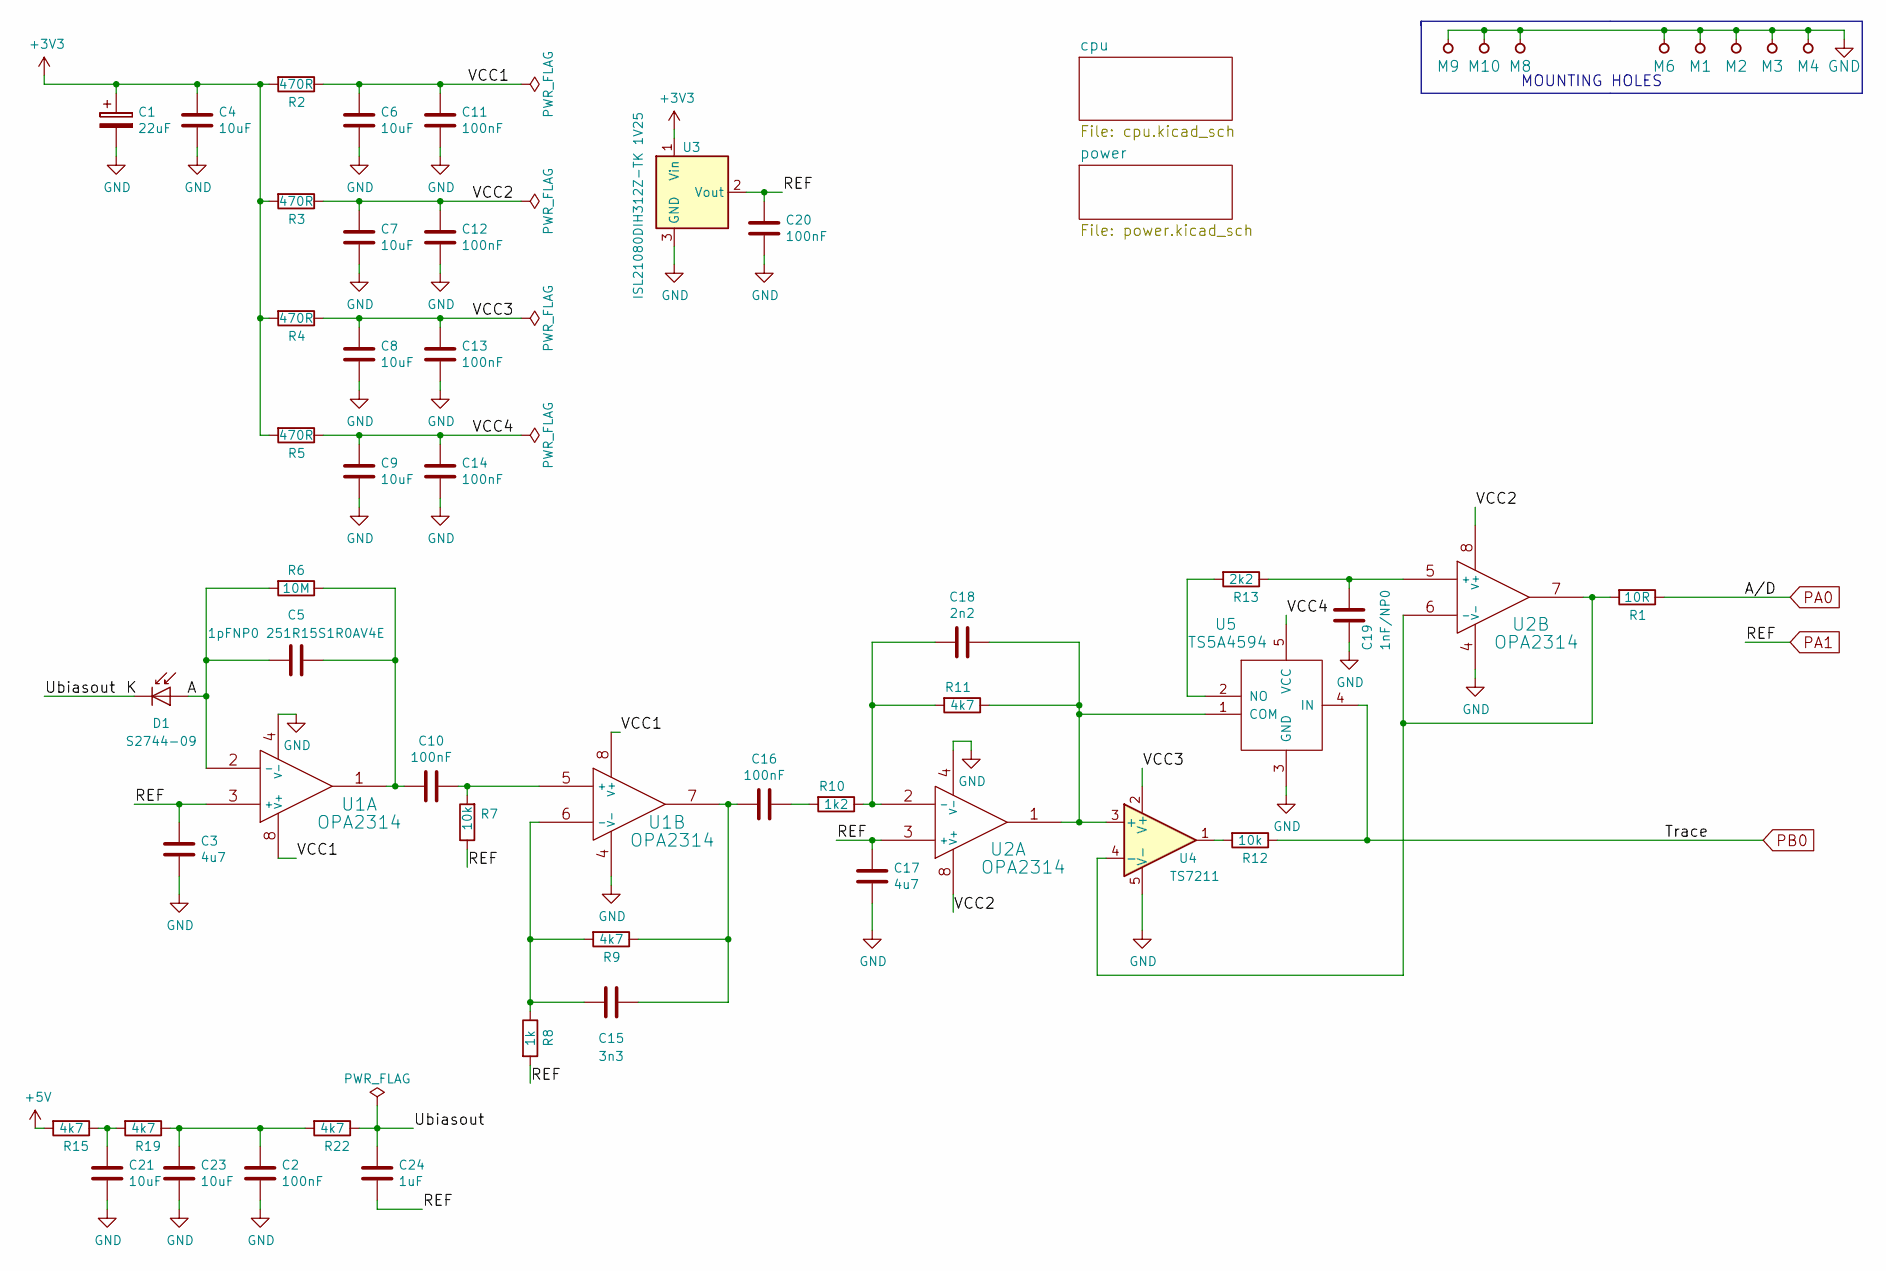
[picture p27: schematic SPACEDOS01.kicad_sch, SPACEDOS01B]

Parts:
C1: 22uF; TantalC_SizeC_Reflow
C2, C10, C11, C12, C13, C14, C16, C20: 100nF; SMD-0805
C3, C17: 4u7; SMD-0805
C4, C6, C7, C8, C9, C21, C23: 10uF; SMD-0805
C5: 1pFNP0 251R15S1R0AV4E; SMD-0805
C15: 3n3; SMD-0805
C18: 2n2; SMD-0805
C19: 1nF/NP0; SMD-0805
C24: 1uF; SMD-0805
D1: S2744-09; HAMAMATSU_S11773-02
M1, M2, M3, M4: HOLE; MountingHole_3mm
M6: BMI-S-210-F
M8, M9, M10: BMI-S-204-F; Laird_Technologies_BMI-S-204-F_32.00x32.00mm
R1: 10R; SMD-0805
R2, R3, R4, R5: 470R; SMD-0805
R6: 10M; SMD-0805
R7, R12: 10k; SMD-0805
R8: 1k; SMD-0805
R9, R11, R15, R19, R22: 4k7; SMD-0805
R10: 1k2; SMD-0805
R13: 2k2; SMD-0805
U1, U2: OPA2314; SOIC-8_3.9x4.9mm_Pitch1.27mm
U3: ISL21080DIH312Z-TK 1V25; SOT-23
U4: TS7211; SOT-23-5_HandSoldering
U5: TS5A4594; SOT-23-5_HandSoldering

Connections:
+3V3: C1.1, C4.1, R2.2, R3.2, R4.2, R5.2, U3.1 (Vin); also elsewhere on the board
+5V: R15.2; also elsewhere on the board
/A: C5.2, D1.2 (A), R6.2, U1.2 (-)
/K: C24.1, D1.1 (K), R22.1
/VCC1: C6.1, C11.1, R2.1, U1.8 (V+)
/VCC2: C7.1, C12.1, R3.1, U2.8 (V+)
/VCC3: C8.1, C13.1, R4.1, U4.2 (V+)
/VCC4: C9.1, C14.1, R5.1, U5.5 (VCC)
GND: C1.2, C2.2, C3.2, C4.2, C6.2, C7.2, C8.2, C9.2, C11.2, C12.2, C13.2, C14.2, C17.2, C19.2, C20.2, C21.2, C23.2, M1.1, M2.1, M3.1, M4.1, M6.1, M8.1, M9.1, M10.1, U1.4 (V-), U2.4 (V-), U3.3 (GND), U4.5 (V-), U5.3 (GND); also elsewhere on the board
unnamed: C2.1, C23.1, R19.1, R22.2
unnamed: C5.1, C10.2, R6.1, U1.1
unnamed: C15.1, C16.2, R9.1, U1.7
unnamed: C16.1, R10.2
unnamed: C21.1, R15.1, R19.2
unnamed: R12.2, U4.1
unnamed: C10.1, R7.2, U1.5 (+)
unnamed: C15.2, R8.1, R9.2, U1.6 (-)
unnamed: C18.2, R10.1, R11.2, U2.2 (-)
unnamed: C19.1, R13.1, U2.5 (+)
unnamed: R1.2, U2.6 (-), U2.7, U4.4 (-)
unnamed: C18.1, R11.1, U2.1, U4.3 (+), U5.1 (COM)
unnamed: R13.2, U5.2 (NO)
PA0: R1.1; also elsewhere on the board
PA1: C3.1, C17.1, C20.1, C24.2, R7.1, R8.2, U1.3 (+), U2.3 (+), U3.2 (Vout); also elsewhere on the board
PB0: R12.1, U5.4 (IN); also elsewhere on the board

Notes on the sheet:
MOUNTING HOLES

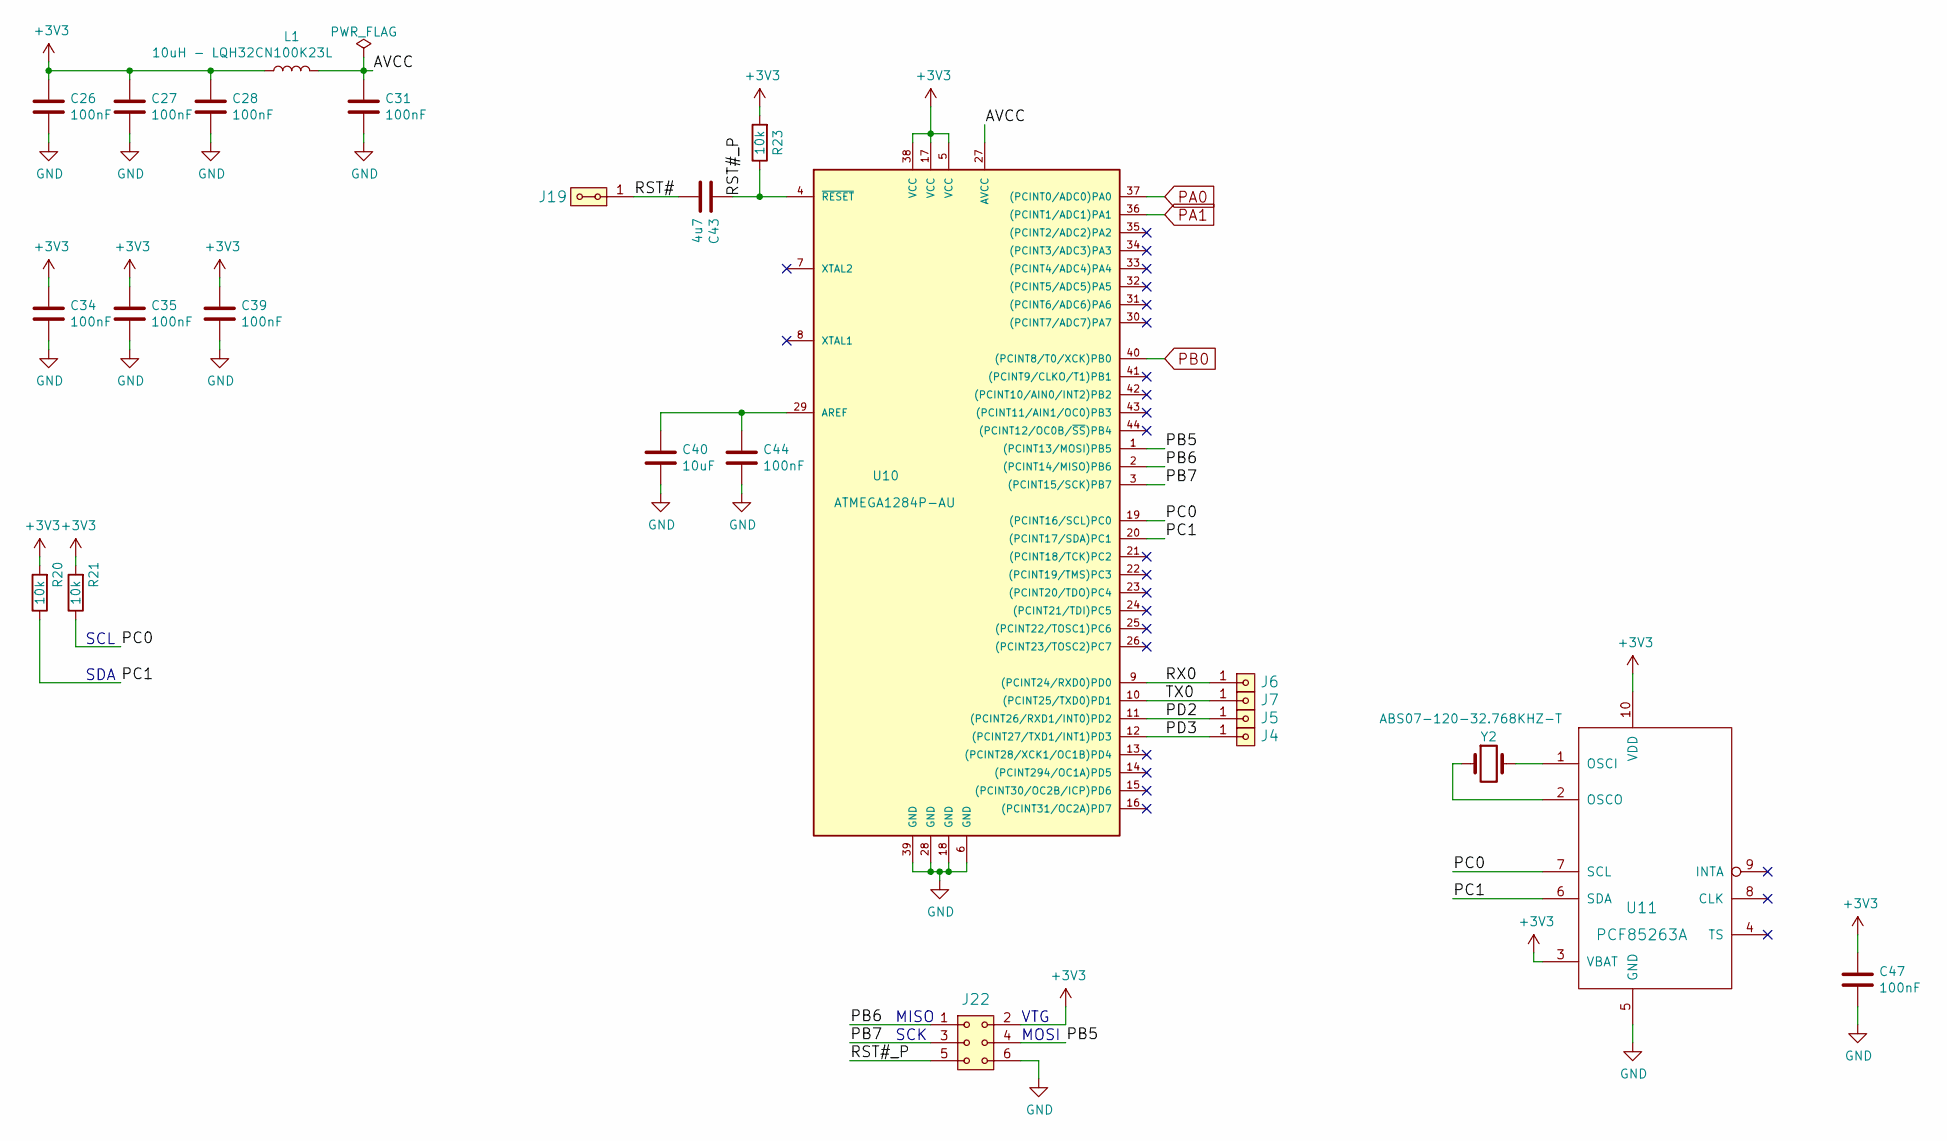
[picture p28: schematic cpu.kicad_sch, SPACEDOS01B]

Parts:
C26, C27, C28, C31, C34, C35, C39, C44, C47: 100nF; SMD-0805
C40: 10uF; SMD-0805
C43: 4u7; SMD-0805
J4, J5, J6, J7: HEADER_1x01; Straight_1x01
J19: HEADER_2x01_PARALLEL; Straight_2x01
J22: HEADER_2x03; SMD_2x03
L1: 10uH - LQH32CN100K23L; SMD-1210
R20, R21, R23: 10k; SMD-0805
U10: ATMEGA1284P-AU; TQFP-44_10x10mm_P0.8mm
U11: PCF85263A; TSSOP-10_3x3mm_Pitch0.5mm
Y2: ABS07-120-32.768KHZ-T; ABS07

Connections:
+3V3: C26.1, C27.1, C28.1, C34.1, C35.1, C39.1, C47.1, J22.2, L1.1, R20.2, R21.2, R23.2, U10.5 (VCC), U10.17 (VCC), U10.38 (VCC), U11.3 (VBAT), U11.10 (VDD); also elsewhere on the board
/cpu/AVCC: C31.1, L1.2, U10.27 (AVCC)
/cpu/PB5: J22.4, U10.1 ((PCINT13/MOSI)PB5)
/cpu/PB6: J22.1, U10.2 ((PCINT14/MISO)PB6)
/cpu/PB7: J22.3, U10.3 ((PCINT15/SCK)PB7)
/cpu/PC0: R21.1, U10.19 ((PCINT16/SCL)PC0), U11.7 (SCL)
/cpu/PC1: R20.1, U10.20 ((PCINT17/SDA)PC1), U11.6 (SDA)
/cpu/PD2: J5.1, U10.11 ((PCINT26/RXD1/INT0)PD2)
/cpu/PD3: J4.1, U10.12 ((PCINT27/TXD1/INT1)PD3)
/cpu/RST#: C43.2, J19.1, J19.2
/cpu/RST#_P: C43.1, J22.5, R23.1, U10.4 (~RESET)
/cpu/RX0: J6.1, U10.9 ((PCINT24/RXD0)PD0)
/cpu/TX0: J7.1, U10.10 ((PCINT25/TXD0)PD1)
GND: C26.2, C27.2, C28.2, C31.2, C34.2, C35.2, C39.2, C40.2, C44.2, C47.2, J22.6, U10.6 (GND), U10.18 (GND), U10.28 (GND), U10.39 (GND), U11.5 (GND); also elsewhere on the board
unnamed: C40.1, C44.1, U10.29 (AREF)
unnamed: U11.1 (OSCI), Y2.2
unnamed: U11.2 (OSCO), Y2.1
PA0: U10.37 ((PCINT0/ADC0)PA0); also elsewhere on the board
PA1: U10.36 ((PCINT1/ADC1)PA1); also elsewhere on the board
PB0: U10.40 ((PCINT8/T0/XCK)PB0); also elsewhere on the board

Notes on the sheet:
SCL
MISO
MOSI
SCK
SDA
VTG

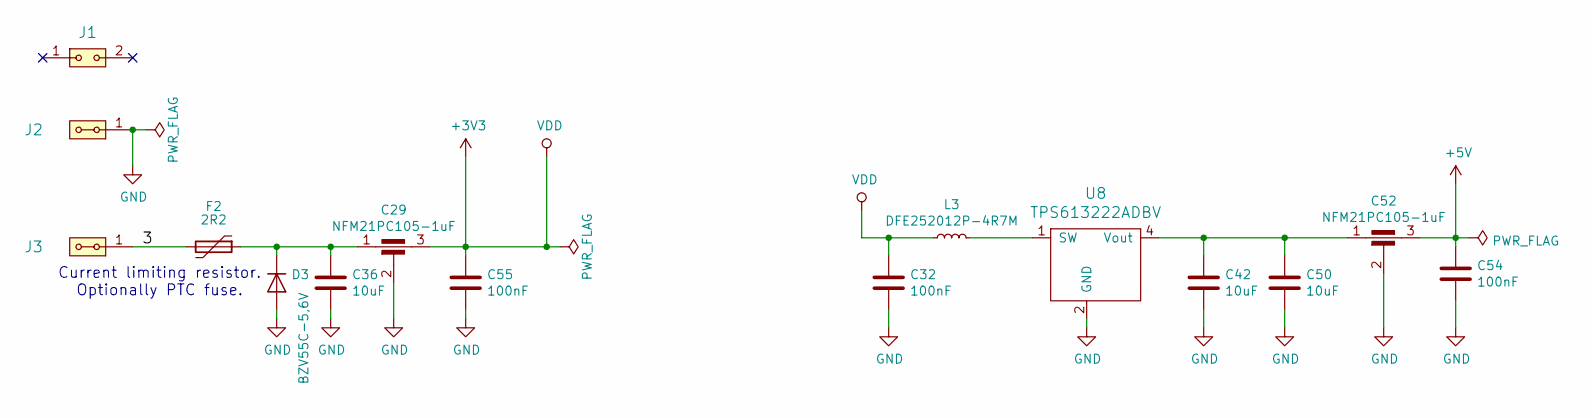
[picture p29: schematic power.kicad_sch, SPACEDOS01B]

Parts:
C29, C52: NFM21PC105-1uF; FIR_0805
C32, C54, C55: 100nF; SMD-0805
C36, C42, C50: 10uF; SMD-0805
D3: BZV55C-5,6V; D_MiniMELF
F2: 2R2; SMD-0805
J1: HEADER_2x01; Straight_1x02
J2, J3: HEADER_2x01_PARALLEL; Straight_1x02
L3: DFE252012P-4R7M; R_0805_2012Metric_Pad1.15x1.40mm_HandSolder
U8: TPS613222ADBV; SOT-23-5

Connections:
+3V3: C29.3, C32.1, C55.1, L3.1; also elsewhere on the board
+5V: C52.3, C54.1; also elsewhere on the board
/power/3: F2.2, J3.1, J3.2
GND: C29.2, C32.2, C36.2, C42.2, C50.2, C52.2, C54.2, C55.2, D3.2 (A), J2.1, J2.2, U8.2 (GND); also elsewhere on the board
unnamed: C29.1, C36.1, D3.1 (K), F2.1
unnamed: L3.2, U8.1 (SW)
unnamed: C42.1, C50.1, C52.1, U8.4 (Vout)

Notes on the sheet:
Current limiting resistor. Optionally PTC fuse.

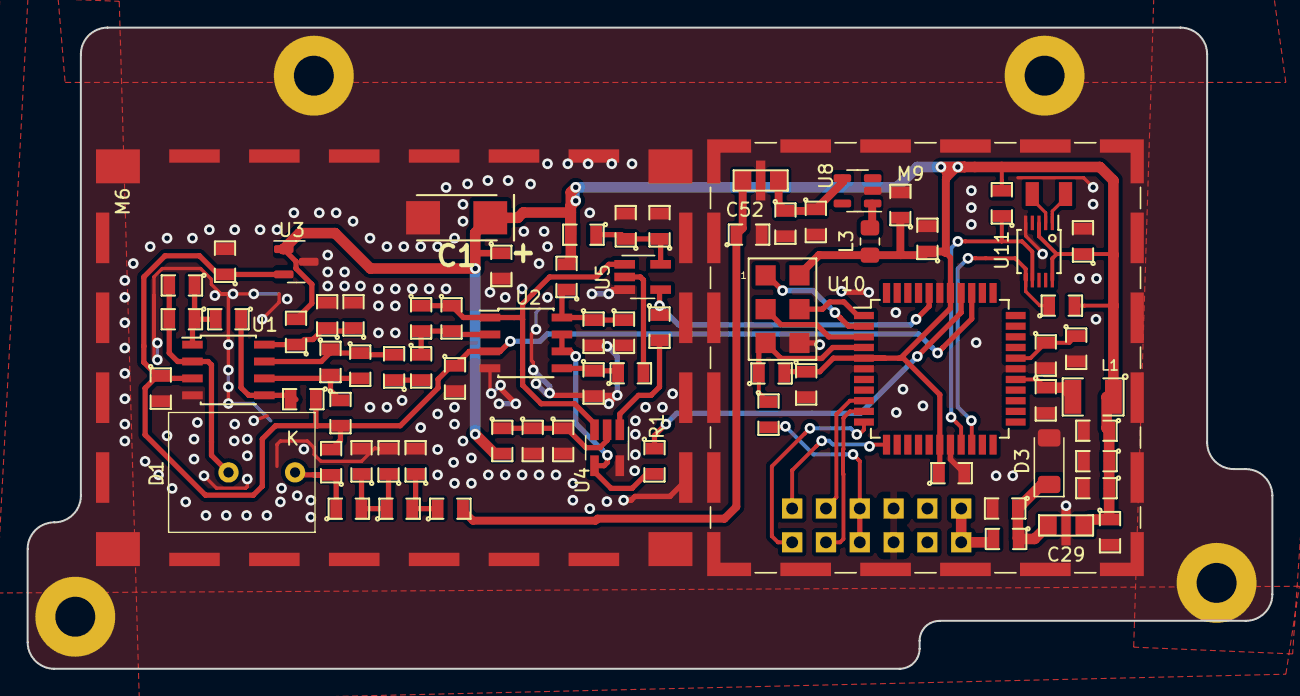
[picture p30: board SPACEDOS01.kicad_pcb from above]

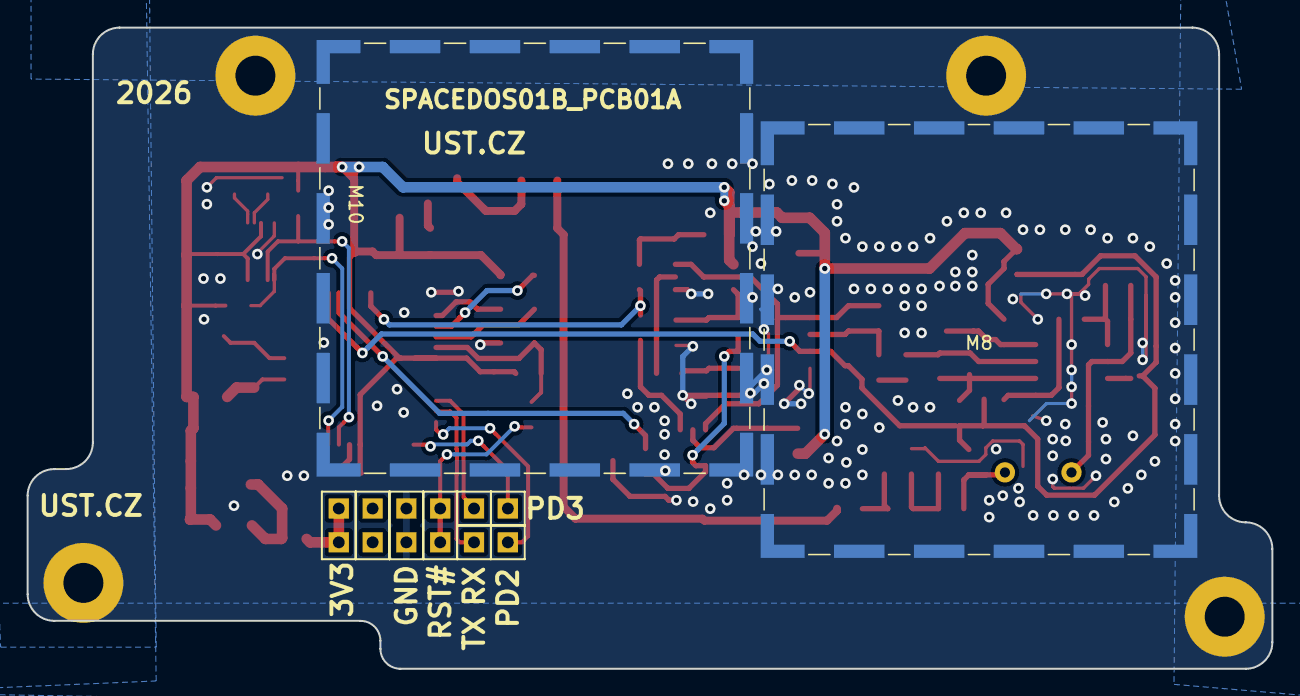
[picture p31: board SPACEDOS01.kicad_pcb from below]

Board: 2 copper layers, 93.5 x 48.2 mm, 92 parts (10 on the bottom side), 44 nets.

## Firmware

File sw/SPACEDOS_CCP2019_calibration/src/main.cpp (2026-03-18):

/*
  SPACEDOS for CCP2019
  for HW: SPACEDOS01A 

  Compiled with: Arduino 1.8.5

  ISP
  ---
  PD0     RX
  PD1     TX
  RESET#  through 50M capacitor to RST#

  ANALOG
  ------
  +      A0  PA0
  -      A1  PA1
  TRACE  0   PB0

                     Mighty 1284p
                      +---\/---+
           (D 0) PB0 1|        |40 PA0 (AI 0 / D24)
           (D 1) PB1 2|        |39 PA1 (AI 1 / D25)
      INT2 (D 2) PB2 3|        |38 PA2 (AI 2 / D26)
       PWM (D 3) PB3 4|        |37 PA3 (AI 3 / D27)
    PWM/SS (D 4) PB4 5|        |36 PA4 (AI 4 / D28)
      MOSI (D 5) PB5 6|        |35 PA5 (AI 5 / D29)
  PWM/MISO (D 6) PB6 7|        |34 PA6 (AI 6 / D30)
   PWM/SCK (D 7) PB7 8|        |33 PA7 (AI 7 / D31)
                 RST 9|        |32 AREF
                VCC 10|        |31 GND
                GND 11|        |30 AVCC
              XTAL2 12|        |29 PC7 (D 23)
              XTAL1 13|        |28 PC6 (D 22)
      RX0 (D 8) PD0 14|        |27 PC5 (D 21) TDI
      TX0 (D 9) PD1 15|        |26 PC4 (D 20) TDO
RX1/INT0 (D 10) PD2 16|        |25 PC3 (D 19) TMS
TX1/INT1 (D 11) PD3 17|        |24 PC2 (D 18) TCK
     PWM (D 12) PD4 18|        |23 PC1 (D 17) SDA
     PWM (D 13) PD5 19|        |22 PC0 (D 16) SCL
     PWM (D 14) PD6 20|        |21 PD7 (D 15) PWM
                      +--------+
*/

#include <Arduino.h>
#include "wiring_private.h"
#include <Wire.h>           // Tested with version 1.0.0. built in
#include "RTClib.h"         // Tested with version 1.5.4. by NeiroN
#include <avr/wdt.h>

String githash = "$Id$";

#define TRACE     0    // PB0
#define PIN_PC7   23   // PC7
#define PIN_PC3   19   // PC3

#define CHANNELS 512   // number of channels in buffer for histogram, including negative numbers
#define RANGE 252      // Dynamic range in channels

uint16_t count = 0;
uint16_t offset, base_offset;
uint8_t lo, hi;
uint16_t u_sensor, maximum;
uint32_t dayly[8], day1[3], day2[3];
uint16_t daylycount = 0;

RTC_Millis rtc;

// Read Analog Differential without gain (read datashet of ATMega1280 and ATMega2560 for refference)
// Use analogReadDiff(NUM)
//  NUM  | POS PIN | NEG PIN | GAIN
//  0    | A0      | A1      | 1x
//  1    | A1      | A1      | 1x
//  2    | A2      | A1      | 1x
//  3    | A3      | A1      | 1x
//  4    | A4      | A1      | 1x
//  5    | A5      | A1      | 1x
//  6    | A6      | A1      | 1x
//  7    | A7      | A1      | 1x
//  8    | A8      | A9      | 1x
//  9    | A9      | A9      | 1x
//  10   | A10     | A9      | 1x
//  11   | A11     | A9      | 1x
//  12   | A12     | A9      | 1x
//  13   | A13     | A9      | 1x
//  14   | A14     | A9      | 1x
//  15   | A15     | A9      | 1x
#define PIN 0
uint8_t analog_reference = INTERNAL2V56; // DEFAULT, INTERNAL, INTERNAL1V1, INTERNAL2V56, or EXTERNAL

void setup()
{

  // Open serial communications and wait for port to open:
  Serial.begin(2400);

  wdt_enable(WDTO_8S); // Enable WDT with 8 second timeout

  Serial.println("$POSD," + githash.substring(5,45)); // FW Git hash

  ADMUX = (analog_reference << 6) | ((PIN | 0x10) & 0x1F);

  ADCSRB = 0;               // Switching ADC to Free Running mode
  sbi(ADCSRA, ADATE);       // ADC autotrigger enable (mandatory for free running mode)
  sbi(ADCSRA, ADSC);        // ADC start the first conversions
  sbi(ADCSRA, 2);           // 0x100 = clock divided by 16, 62.5 kHz, 208 us for 13 cycles of one AD conversion, 24 us fo 1.5 cycle for sample-hold
  cbi(ADCSRA, 1);
  cbi(ADCSRA, 0);

  pinMode(TRACE, OUTPUT);   // TRACE for peak detetor
  pinMode(PIN_PC7, INPUT);  // spare input port
  digitalWrite(PIN_PC3, LOW);   // turn the output port low
  pinMode(PIN_PC3, OUTPUT); // spare output port
 
  digitalWrite(TRACE, LOW);

  // measurement of ADC offset
  ADMUX = (analog_reference << 6) | 0b10001; // Select +A1,-A1 for offset correction
  delay(200);
  ADCSRB = 0;               // Switching ADC to Free Running mode
  sbi(ADCSRA, ADATE);       // ADC autotrigger enable (mandatory for free running mode)
  sbi(ADCSRA, ADSC);        // ADC start the first conversions
  sbi(ADCSRA, 2);           // 0x100 = clock divided by 16, 62.5 kHz, 208 us for 13 cycles of one AD conversion, 24 us fo 1.5 cycle for sample-hold
  cbi(ADCSRA, 1);
  cbi(ADCSRA, 0);
  sbi(ADCSRA, ADIF);                  // reset interrupt flag from ADC
  while (bit_is_clear(ADCSRA, ADIF)); // wait for the first conversion
  sbi(ADCSRA, ADIF);                  // reset interrupt flag from ADC
  lo = ADCL;
  hi = ADCH;
  ADMUX = (analog_reference << 6) | 0b10000; // Select +A0,-A1 for measurement
  ADCSRB = 0;               // Switching ADC to Free Running mode
  sbi(ADCSRA, ADATE);       // ADC autotrigger enable (mandatory for free running mode)
  sbi(ADCSRA, ADSC);        // ADC start the first conversions
  sbi(ADCSRA, 2);           // 0x100 = clock divided by 16, 62.5 kHz, 208 us for 13 cycles of one AD conversion, 24 us fo 1.5 cycle for sample-hold
  cbi(ADCSRA, 1);
  cbi(ADCSRA, 0);
  // combine the two bytes
  u_sensor = (hi << 7) | (lo >> 1);
  // manage negative values
  if (u_sensor <= (CHANNELS / 2) - 1 ) {
    u_sensor += (CHANNELS / 2);
  } else {
    u_sensor -= (CHANNELS / 2);
  }
  base_offset = u_sensor - 2;

  for (int n = 0; n < 8; n++) // Reset dayly flux counts
  {
    dayly[n] = 0;
  }

  for (int n = 0; n < 3; n++) // Reset dayly circular buffer
  {
    day1[n] = 0;
    day2[n] = 0;
  }

  
  Serial.println("$ICSD");
}


void loop()
{
  uint16_t buffer[CHANNELS];

  for (int n = 0; n < CHANNELS; n++) // Reset buffer for histogram
  {
    buffer[n] = 0;
  }

  // measurement of ADC offset
  ADMUX = (analog_reference << 6) | 0b10001; // Select +A1,-A1 for offset correction
  delay(50);
  ADCSRB = 0;               // Switching ADC to Free Running mode
  sbi(ADCSRA, ADATE);       // ADC autotrigger enable (mandatory for free running mode)
  sbi(ADCSRA, ADSC);        // ADC start the first conversions
  sbi(ADCSRA, 2);           // 0x100 = clock divided by 16, 62.5 kHz, 208 us for 13 cycles of one AD conversion, 24 us fo 1.5 cycle for sample-hold
  cbi(ADCSRA, 1);
  cbi(ADCSRA, 0);
  sbi(ADCSRA, ADIF);                  // reset interrupt flag from ADC
  while (bit_is_clear(ADCSRA, ADIF)); // wait for the first conversion
  sbi(ADCSRA, ADIF);                  // reset interrupt flag from ADC
  lo = ADCL;
  hi = ADCH;
  ADMUX = (analog_reference << 6) | 0b10000; // Select +A0,-A1 for measurement
  ADCSRB = 0;               // Switching ADC to Free Running mode
  sbi(ADCSRA, ADATE);       // ADC autotrigger enable (mandatory for free running mode)
  sbi(ADCSRA, ADSC);        // ADC start the first conversions
  sbi(ADCSRA, 2);           // 0x100 = clock divided by 16, 62.5 kHz, 208 us for 13 cycles of one AD conversion, 24 us fo 1.5 cycle for sample-hold
  cbi(ADCSRA, 1);
  cbi(ADCSRA, 0);
  // combine the two bytes
  u_sensor = (hi << 7) | (lo >> 1);
  // manage negative values
  if (u_sensor <= (CHANNELS / 2) - 1 ) {
    u_sensor += (CHANNELS / 2);
  } else {
    u_sensor -= (CHANNELS / 2);
  }
  offset = u_sensor;

  PORTB = 1;                          // Set RESET/TRACE output for peak detector to H
  sbi(ADCSRA, ADIF);                  // reset interrupt flag from ADC
  while (bit_is_clear(ADCSRA, ADIF)); // wait for the first dummy conversion
  DDRB = 0b10011111;                  // RESET/TRACE peak detector
  delayMicroseconds(100);             // guaranteed reset
  DDRB = 0b10011110;

  sbi(ADCSRA, ADIF);        // reset interrupt flag from ADC

  uint16_t suppress = 0;

  // dosimeter integration
  //for (uint8_t i = 0; i < 6; i++) // multiple of 5 s
  {
    while (bit_is_clear(ADCSRA, ADIF)); // wait for dummy conversion
    DDRB = 0b10011111;                  // RESET/TRACE peak detector
    asm("NOP");                         // cca 6 us for 2k2 resistor and 1k capacitor in peak detector
    asm("NOP");
    asm("NOP");
    asm("NOP");
    asm("NOP");
    DDRB = 0b10011110;
    sbi(ADCSRA, ADIF);                  // reset interrupt flag from ADC

    for (uint16_t n = 0; n < 65535; n++) // 4600 = cca 1 s
    {
      while (bit_is_clear(ADCSRA, ADIF)); // wait for end of conversion
      //delayMicroseconds(24);            // 24 us wait for 1.5 cycle of 62.5 kHz ADC clock for sample/hold for next conversion
      asm("NOP");                         // cca 8 us after loop
      asm("NOP");
      asm("NOP");
      asm("NOP");
      asm("NOP");
      asm("NOP");

      DDRB = 0b10011111;                  // RESET/TRACE peak detector
      asm("NOP");                         // cca 7 us for 2k2 resistor and 100n capacitor in peak detector
      asm("NOP");
      asm("NOP");
      asm("NOP");
      asm("NOP");
      DDRB = 0b10011110;
      sbi(ADCSRA, ADIF);                  // reset interrupt flag from ADC

      // we have to read ADCL first; doing so locks both ADCL
      // and ADCH until ADCH is read.  reading ADCL second would
      // cause the results of each conversion to be discarded,
      // as ADCL and ADCH would be locked when it completed.
      lo = ADCL;
      hi = ADCH;

      // combine the two bytes
      u_sensor = (hi << 7) | (lo >> 1);

      // manage negative values
      if (u_sensor <= (CHANNELS / 2) - 1 ) 
      {
        u_sensor += (CHANNELS / 2);
      } 
      else 
      {
        u_sensor -= (CHANNELS / 2);
      }

      if (u_sensor > maximum) // filter double detection for pulses between two samples
      {
        maximum = u_sensor;
        suppress++;
      }
      else
      {
        buffer[maximum]++;
        maximum = 0;
      }
      wdt_reset(); //Reset WDT 
    }
  }

  // Data out
  {
    DateTime now = rtc.now();
    uint32_t uptime;
    uptime = now.unixtime();

    // make a string for assembling the data to log
    // HexaDecimal Compressed Spectrum
    String dataString = "$DPSD,";

    dataString += String(uptime, HEX);;
    dataString += ",";

    uint16_t noise = base_offset + 3;
    uint16_t energy = 0;

    // noise
    dataString += String(buffer[noise-1], HEX);
    dataString += ",";

    // 0.1 MeV
    dataString += String(buffer[noise], HEX);
    dayly[0] += buffer[noise];
    dataString += ",";

    // 0.14 MeV
    for (uint16_t n = noise + 1; n < (noise + 3); n++)
    {
      energy += buffer[n];
    }
    dataString += String(energy, HEX);
    dayly[1] += energy;
    dataString += ",";
    energy = 0;

    // 0.21 MeV
    for (uint16_t n = noise + 3; n < (noise + 6); n++)
    {
      energy += buffer[n];
    }
    dataString += String(energy, HEX);
    dayly[2] += energy;
    dataString += ",";
    energy = 0;

    // 0.33 MeV
    for (uint16_t n = noise + 6; n < (noise + 15); n++)
    {
      energy += buffer[n];
    }
    dataString += String(energy, HEX);
    dayly[3] += energy;
    dataString += ",";
    energy = 0;

    // 0.66 MeV
    for (uint16_t n = noise + 15; n < (noise + 42); n++)
    {
      energy += buffer[n];
    }
    dataString += String(energy, HEX);
    dayly[4] += energy;
    dataString += ",";
    energy = 0;

    // 1.68 MeV
    for (uint16_t n = noise + 42; n < (noise + 123); n++)
    {
      energy += buffer[n];
    }
    dataString += String(energy, HEX);
    dayly[5] += energy;
    dataString += ",";
    energy = 0;

    // 4.72 MeV
    for (uint16_t n = noise + 123; n < (noise + 236); n++)
    {
      energy += buffer[n];
    }
    dataString += String(energy, HEX);
    dayly[6] += energy;
    dataString += ",";
    energy = 0;

    // 9 MeV
    for (int16_t n = noise + 236; n < (CHANNELS); n++)
    {
      energy += buffer[n];
    }
    dataString += String(energy, HEX);
    dayly[7] += energy;
    dataString += ",";
    energy = 0;

    dataString += String(offset, HEX);

    Serial.println(dataString);  // print-out data

    // Decimal spectrum for Housekeeping
    dataString = "$HKSD,";
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

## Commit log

2019-01-30 New PCB
    [SPACEDOS01A_PCB01A.kicad_pcb, SPACEDOS01A_PCB01A.sch, cpu.sch, power.sch]
2019-02-11 connector header
2019-03-06 edit PCB
    [SPACEDOS01B_PCB01A-B_Cu.gbr, SPACEDOS01B_PCB01A-B_Mask.gbr, SPACEDOS01B_PCB01A-Edge_Cuts.gbr, SPACEDOS01B_PCB01A-F_Cu.gbr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]
2019-03-14 FW for calibration and gitattributes for branch master
2019-07-03 Update of device photos.
2021-11-08 Update stylesheet.
    [SPACEDOS01B_PCB01A.kicad_sch, cpu.kicad_sch, cpu.sch, power.kicad_sch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]
2021-12-10 Update kicad project and schematics PDF export.
    [SPACEDOS01B_PCB01A.kicad_sch, cpu.kicad_sch, power.kicad_sch]
2023-01-26 Update designs to KiCAD 6. Update schematics datasheet links Minor schematics improvements (titleblocks, schematics layout)
    [SPACEDOS01B_PCB01A.kicad_pcb, SPACEDOS01B_PCB01A.kicad_sch, cpu.kicad_sch, power.kicad_sch]
2023-01-26 Correcly setup automation workflows and cleanup KiCAD project.
    [SPACEDOS01B_PCB01A.kicad_sch, SPACEDOS01B_PCB01A.sch, cpu.kicad_sch, power.kicad_sch]
2023-01-26 Update actions products
    [SPACEDOS01B_PCB01A-B_Courtyard.dxf, SPACEDOS01B_PCB01A-B_Cu.dxf, SPACEDOS01B_PCB01A-B_Fab.dxf, SPACEDOS01B_PCB01A-B_Mask.dxf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]
2024-02-09 Update project files.
    [SPACEDOS01B_PCB01A.kicad_pcb]
2024-02-09 Center PCB in page. Improve dimensions.
    [SPACEDOS01B_PCB01A.kicad_pcb, SPACEDOS01B_PCB01A.kicad_sch, cpu.kicad_sch, power.kicad_sch]
2024-02-09 Update workflows.
    [SPACEDOS01B_PCB01A.kicad_pcb]
2024-02-09 Project renamed to allow use of standard workflow.
    [SPACEDOS01.kicad_pcb, SPACEDOS01.kicad_sch, SPACEDOS01B_PCB01A-B.Cu.gbr, SPACEDOS01B_PCB01A-B.Mask.gbr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]
2024-02-09 Updated PCB dimensions.
    [SPACEDOS01.kicad_pcb]
2024-02-09 Improve documentation image.
    [SPACEDOS01.kicad_pcb]
2025-12-15 update ustid
    [SPACEDOS01.kicad_sch, cpu.kicad_sch, power.kicad_sch]
2026-01-30 Update titleblock to fix schematics PDF generation. Improve schematics layout.
    [SPACEDOS01.kicad_sch, cpu.kicad_sch]
2026-01-31 Improve schematics desription.
    [power.kicad_sch]
2026-03-12 Update project. Update components IDs
    [SPACEDOS01.kicad_pcb, SPACEDOS01.kicad_sch]
2026-03-18 version as delivered
    [SPACEDOS01_20260228_205218_1k2_PU_0.csv, SPACEDOS01_20260316_184526_SN2_PU.csv, SPACEDOS01_20260316_191008_SN3_PU.csv, combined_spectrum.csv]
